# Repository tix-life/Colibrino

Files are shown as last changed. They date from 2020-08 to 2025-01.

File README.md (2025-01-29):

# Colibrino 
Esse é um projeto open-source de uma versão *Faça você mesmo* do nosso mouse de cabeça o Colibri! O objetivo principal dele é promover acessibilidade para pessoas com deficiências físicas do como tetraplegia, artrogripose, amputações e parilisia cerebral.

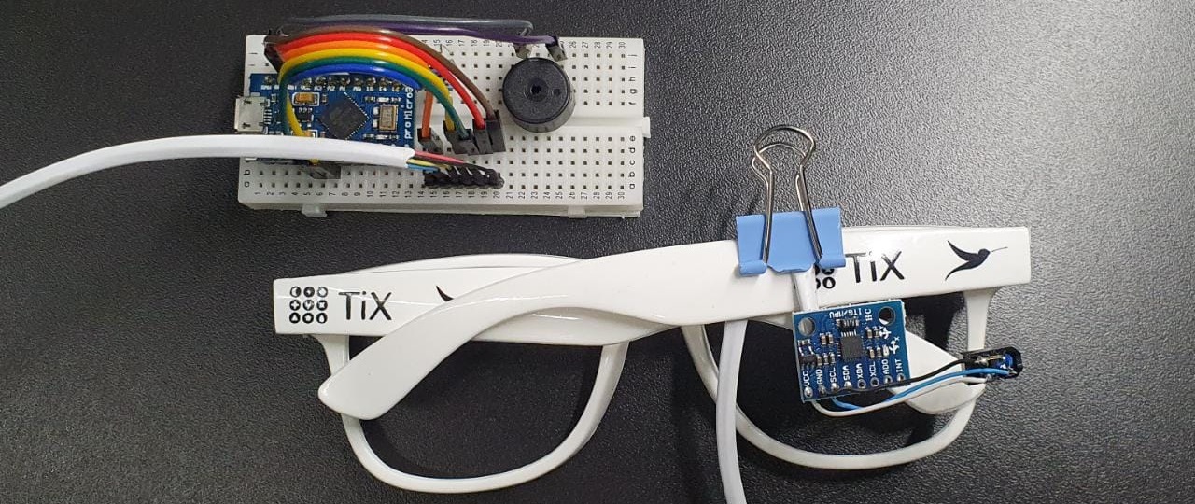
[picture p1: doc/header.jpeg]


[Compartilhe sua montagem e suas dúvidas no nosso fórum!](https://groups.google.com/g/colibrino) 

# Índice 

- [Colibrino](#colibrino)
- [Índice](#índice)
- [Licença de Uso](#licença-de-uso)
- [Materiais](#materiais)
- [Montagem](#montagem)
  - [Diagrama Esquemático](#diagrama-esquemático)
  - [Instruções de Montagem](#instruções-de-montagem)
- [Modo de Uso](#modo-de-uso)
- [Plano de Voo 🐦](#plano-de-voo-)
- [Materiais de referência](#materiais-de-referência)

# Licença de Uso
Este programa é um software livre. Você pode redistribuí-lo e/ou
modificá-lo sob os termos da Licença Pública Geral GNU como publicada
pela Free Software Foundation; na versão 3 da Licença, ou
(a seu critério) qualquer versão posterior.

Este programa é distribuído na esperança de que possa ser útil,
mas SEM NENHUMA GARANTIA; sem uma garantia implícita de ADEQUAÇÃO
a qualquer MERCADO ou APLICAÇÃO EM PARTICULAR. Veja a
[Licença Pública Geral GNU](https://github.com/tix-life/Colibrino/blob/master/LICENSE) para mais detalhes.

# Materiais:

|Nome|Especificação|Documentação|
|---|---|---|
|Arduino Leonardo ou Micro Pro|Com Microcontrolador Atmega 32U4|[Pinagem Pro Micro](https://cdn.sparkfun.com/assets/f/d/8/0/d/ProMicro16MHzv2.pdf)<br>[Pinagem Leonardo](https://content.arduino.cc/assets/Pinout-Leonardo_latest.png)|
|MPU6050|Acelerômetro e Giroscópio|[datasheet](https://invensense.tdk.com/wp-content/uploads/2015/02/MPU-6000-Register-Map1.pdf)|
|TCRT 5000|Sensor Infravermelho|[datasheet](https://www.vishay.com/docs/83760/tcrt5000.pdf)|
|Cabo com 6 vias|Ligação entre o Arduino e os Sensores - |[Ex.: cabo para alarme](https://stecondutores.com.br/produto/cabo-de-alarme/)|
|Placa padrão ou protoboard|Base para montagem do circuito||
|Leds|Indicador de piscada e de funcionamento||
|Resistor|1 x 4700Ω a 6800Ω - polarização do fototransistor <br> 1 x 220Ω a 330Ω - restringe corrente do LED IR<br> 1 x 10Ω - atenuar o  buzzer||
|Buzzer|Indicador Sonoro da Piscada||
|Cabo USB|Conexão entre computador e Arduíno||
|Armação de Óculos|Suporte para os sensores||

# Montagem:

Thumbnail do vídeo (https://www.youtube.com/watch?v=DUF2yonN9Ps)
[Vídeo tutorial](https://www.youtube.com/watch?v=DUF2yonN9Ps)

## Diagrama Esquemático
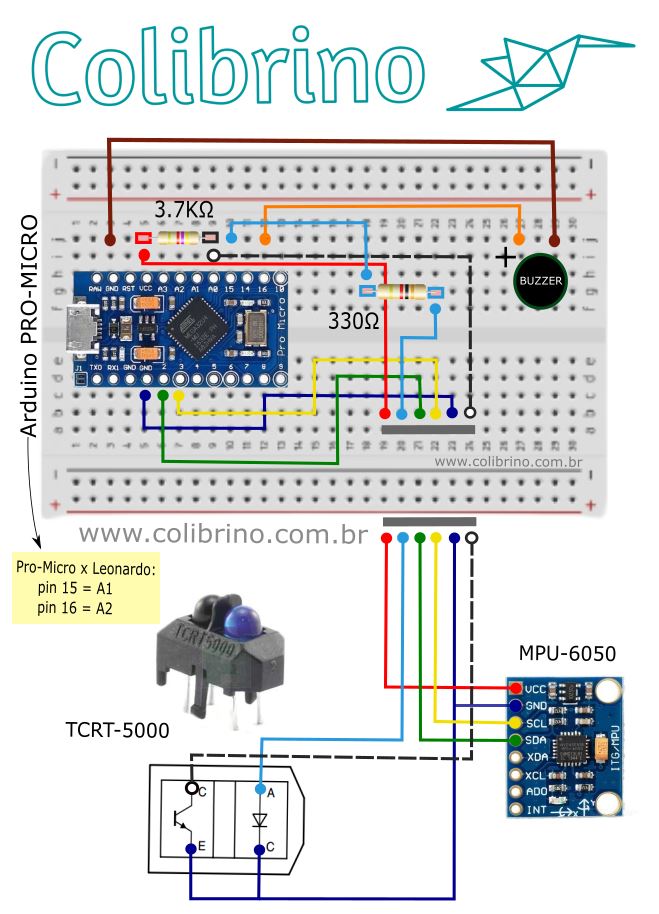
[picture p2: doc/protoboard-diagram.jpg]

## Tabela de Conexões
Nome do Pino no Arduino|Componentes Conectados|Resistor?
|---|---|---|
|VCC (3.3 ou 5V)|MPU-6050 VCC|  |
|VCC (3.3 ou 5V)|TCRT5000 Coletor do Fototransistor| 3500Ω a 5000Ω |
|GND |MPU-6050 GND| |
|GND |TCRT5000 Emissor do Fototransistor| |
|GND |TCRT5000 Cátodo do LED IR (-)|  |
|GND |Buzzer (-)| |
|16 |Buzzer (+)| 0Ω a 10Ω |
|15 |TCRT5000 Ânodo do LED IR (+)| 180Ω a 330Ω |
|A0 |TCRT5000 Coletor do Fototransistor| |

## Instruções de Montagem
1. Conecte o Arduíno, Buzzer, Leds e Resistores no Protoboard. 
2. Para os sensores MPU6050 e TCRT 5000 é necessário solda-los com o fio de 6 vias.
3. Realize as coneções mostradas no diagrama acima.
4. Conecte o Arduíno ao PC usando o cabo USB.
5. Grave o firmware no Arduino usando o [Arduino IDE](https://www.arduino.cc/en/software). No menu "Ferramentas", escolha a opção Arduino Leonardo na lista de placas.
6. Instale o código utilizando o ambiente de desenvolvimento do Arduino devidamente configurado para a placa que está sendo usada.
7. Deixe o Colibrino parado numa mesa sem perturbações até que um beep sonoro indique que ele está pronto para uso (nesse momento ele está calibrando). A calibração é feita apenas uma vez e se não ficar boa (Cursor andando sozinho em alguma direção mesmo o collibrino parado) siga as intruções na seção Calibração.
8. Fixe o sensor MPU6050 em alguma armação de óculos.
9. Use e aproveite. :D
10. [Compartilhe sua montagem e suas dúvidas no nosso fórum!](https://groups.google.com/g/colibrino) 

(montar um painel com imagens)

# Princípios de funcionamento
## Captura do movimento da cabeça
O Colibrino utiliza um tipo de sensor chamado de IMU (Unidade de Medidas Inerciais) para obter informação sobre a orientação espacial da cabeça. A IMU do Colibrino é o MPU-6050, um circuito integrado (acelerômetro + giroscópio) contendo estruturas mecânicas microscópicas capazes de sentir movimentos do corpo preso a ele e a força da gravidade. Essas estruturas mecânicas também interagem eletricamente com o circuito que mede os movimentos em números correspondentes à aceleração e à velocidade angular em três eixos. Os dados são filtrados e utilizados para calcular a posição da cabeça e, por fim, mover o cursor do mouse de forma correspondente.

## Detecção da piscadela
O sensor de piscadelas detecta pequenas variações na reflexão de luz que ocorrem quando uma piscada bem forte é realizada em frente ao sensor. Primeiro a luz infravermelha é emitida por um LED no TCRT5000. A luz é pulsante para que o programa consiga comparar a reflexão com o LED aceso e apagado de forma a compensar variações da luz ambiente. Após ser refletida, a luz é captada por um fototransistor que converte a intensidade da luz em um sinal elétrico medido pelo Arduino.

## ⚠️ Calibração

A calibração efetuada após a primeira gravação do programa no colibrino é feita apenas uma vez. Contudo ela pode falhar devido a movimentações no colibrino durante o processo de calibração, levando a um mau funcionamento do aparelho. Para resolver isso , grave o código LimparCalibração que está dentro da pasta baixada e regrave o código principal mais uma vez. Isso levará o Colibrino para a mesma fase inicial de calibração, repita o procedimento de esperar até que o tempo de calibração conclua.

# Modo de Uso
Com o colibrino devidamente montado para usá-lo basta mexer a cabeça com o oculos que está instalado o sensor. Contudo, segue abaixo uma lista de orientações.

1. O Sensor MPU6050 deve estar colocado no óculos que vai ser usado, porém o TCRT deve estar conectado somente ao fio permitindo o ajuste.
2. Para melhor detecção da piscadela é necessário mexer o fio que o sensor TCRT está conectado para mais próximo ao olho.

(explicar como que usa o colibrino - como posicionar e ajustar o sensor)

# Plano de Voo 🐦
Existe inumeras funções que podem ser adcionadas ao Colibrino e algumas que estão no plano de voo da nossa equipe são:
* Scroll ao inclinar a cabeça para os lados
* Funções com gestos da cabeça

Estamos abertos a sugestões e feedbacks a todos :D 
Agradecemos a leitura <3

# FAQ
* Dúvidas frequentes anexadas no documento abaixo: https://docs.google.com/document/d/1n8rUOnNmSkuknlO98TbDd7EEdKiDvEBH_lRSuz5WyO0/edit?usp=sharing

# Materiais de referência:
* https://www.youtube.com/watch?v=4sIkW7wogrE
* https://github.com/witnessmenow/arduino-switcheroonie/blob/master/BLE-switcheroonie/BLE-switcheroonie.ino
* https://github.com/T-vK/ESP32-BLE-Mouse

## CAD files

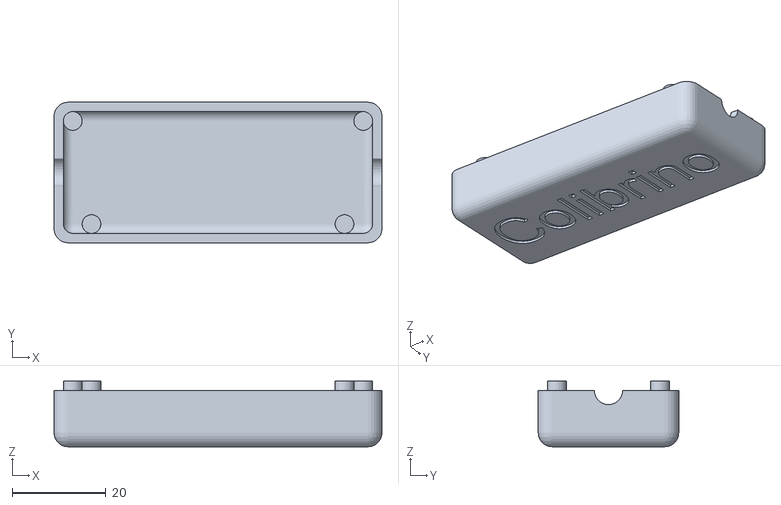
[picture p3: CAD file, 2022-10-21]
3d models/Arduino pro micro box boardless assembly.stl
70.0 x 30.0 x 14.0

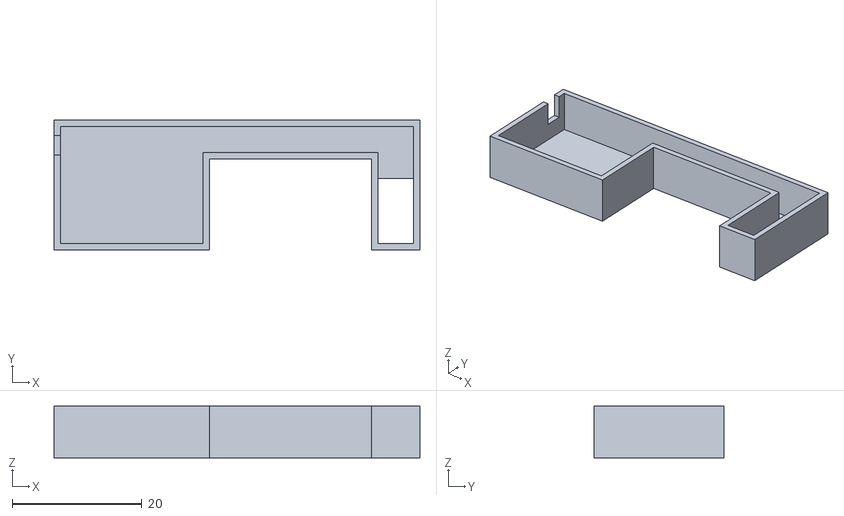
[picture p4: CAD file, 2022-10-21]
3d models/Sensor box IMU and IR part cavity.stl
56.5 x 20.0 x 8.00

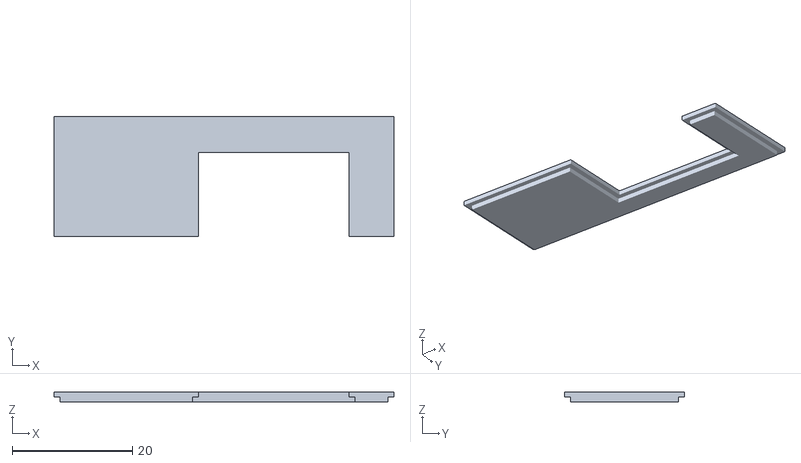
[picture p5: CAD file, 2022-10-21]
3d models/Sensor box IMU and IR part lid.stl
56.5 x 20.0 x 1.60

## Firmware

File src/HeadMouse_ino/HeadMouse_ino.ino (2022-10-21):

// This file is part of the Colibrino project.

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
#include "Mouse.h"
//Carrega a biblioteca Wire
#include <Wire.h>
// #include "filters.h"
#include "MahonyAHRS.h"
#include"mpu6050.h"

//---------------------------------------------------------------------------------------------------
//Definitions
//Mouse
#define SENSIBILIDADE  30
#define TEMPO_DWELL_CICK_MS 1000 
#define DWELL_CICK false
//
#define MPU6050_ACC_GAIN 16384.0
#define MPU6050_GYRO_GAIN 131.072 
/*********************************************************************
 * Global variables
 */
float axR, ayR, azR, gxR, gyR, gzR;
float axg, ayg, azg, gxrs, gyrs, gzrs;
//float ax_filtro, ay_filtro, az_filtro, gx_filtro, gy_filtro, gz_filtro;
bool conectado = false;
//float yaw_filtro, pitch_filtro, roll_filtro;
const int MPU_addr=0x68;  // I2C address of the MPU-6050
/*********************************************************************
 * External variables
 */
extern int16_t AcX, AcY, AcZ, Tmp, GyX, GyY, GyZ;
extern float yaw_mahony,pitch_mahony,roll_mahony;
//Objects
// BleMouse bleMouse;
// filters pbax,pbay,pbaz,pbgx,pbgy,pbgz;

#define INTERRUPT_PIN 7 // use pin 2 on Arduino Uno & most boards
#define LED_PIN 8 // (Arduino is 13, Teensy is 11, Teensy++ is 6)

#define ON true
#define OFF false
int g_clique = 0;
void filtraIMU()
{
  //Filtro 2 ordem
  // ax_filtro= filtro_2PB10Hz(AcX, pbax);
  // ay_filtro= filtro_2PB10Hz(AcY, pbay);
  // az_filtro= filtro_2PB10Hz(AcZ, pbaz);
  // gx_filtro= filtro_2PB10Hz(GyX, pbgx);
  // gy_filtro= filtro_2PB10Hz(GyY, pbgy);
  // gz_filtro= filtro_2PB10Hz(GyZ, pbgz);
  
  //Converte
  axg = (float)(AcX /*- LSM6DSM_AXOFFSET*/) / MPU6050_ACC_GAIN;
  ayg = (float)(AcY /*- LSM6DSM_AYOFFSET*/) / MPU6050_ACC_GAIN;
  azg = (float)(AcZ /*- LSM6DSM_AZOFFSET*/) / MPU6050_ACC_GAIN;
  gxrs = (float)(GyX - (0)) / MPU6050_GYRO_GAIN * 0.01745329; //degree to radians
  gyrs = (float)(GyY - (0)) / MPU6050_GYRO_GAIN * 0.01745329; //degree to radians
  gzrs = (float)(GyZ - (0)) / MPU6050_GYRO_GAIN * 0.01745329; //degree to radians
  // Degree to Radians Pi / 180 = 0.01745329 0.01745329251994329576923690768489
}
float corrigeYaw(float sinal)
{
  static float valorDeriv = 0, zero = 0;
  static float sinalCorrigido=0, offset = 0;
  static float  sinalAnterior = 0;
  static int s=1,d=-1;
  
  valorDeriv = (sinal - zero);
  zero = sinal;
  
  if(valorDeriv <= -180)
  {
      offset += +360.0f;
  }
  else if(valorDeriv >= 180)
  {
      offset += -360.0f;
  }
  sinalCorrigido = sinal;
  sinalCorrigido += offset;
  
  return sinalCorrigido;
}
int8_t mouseHoriz(void)
{
  static float horzZero =0.0f;
  static float horzValue = 0.0f;  // Stores current analog output of each axis
  static float yaw_corrigido = 0.0f;
  static int amostragem = 5;
  yaw_corrigido = corrigePitch(yaw_mahony);
  
  if(--amostragem == 0)
  {
    amostragem = 5;
    horzValue = (yaw_corrigido - horzZero)*SENSIBILIDADE;
    horzZero = yaw_corrigido;
  }
  return horzValue;
}
float corrigePitch(float sinal)
{
  static float valorDeriv = 0, zero = 0;
  static float sinalCorrigido=0, offset = 0;
  static float  sinalAnterior = 0;
  static int s=1,d=-1;
  
  valorDeriv = (sinal - zero);
  zero = sinal;

  if(valorDeriv <= -180)
  {
      offset += +360.0f;
  }
  else if(valorDeriv >= 180)
  {
      offset += -360.0f;
  }
  sinalCorrigido = sinal;
  sinalCorrigido += offset;
  
  return sinalCorrigido;
}
int8_t mouseVert(void)
{
  static float vertZero =0.0f;
  static float vertValue = 0.0f;  // Stores current analog output of each axis
  static float pitch_corrigido = 0.0f;
  static int amostragem = 5;
  pitch_corrigido = corrigePitch(pitch_mahony);
  if(--amostragem == 0)
  {
    amostragem = 5;
    vertValue = (pitch_corrigido - vertZero)*SENSIBILIDADE;
    vertZero = pitch_corrigido;
  }
  return vertValue;
}


/*********************************************************************
 * @fn      scrollDetector
 * 
 * @brief   Ativa ou reativa o Colibri de acordo com a 
 *          sequencia de movimentos feita
 *
 * @param   horz - derivada do Yaw
 * @param   verti - derivada do Pitch
 *
 * @return  ligado - flag para ativar/desativar o colibri.
 */
#define RMEDIA 0.001f
#define RMARGEM 4
int scrollDetector() {
  static float rmedia = 90;
  static uint32_t timer1 = 0;
  int diferenca;
  
  diferenca = roll_mahony - rmedia;
  
  
            //SendInt(diferenca);
         //SendLineEnd();
  
  if (abs(diferenca) < RMARGEM) {
    rmedia = ((1 - RMEDIA) * rmedia) + (RMEDIA * roll_mahony);
    timer1 = millis();
    return 0;
  }
  else if (abs(diferenca) > 2.5*RMARGEM) { // Ignora roll muito grande
    if (millis() - timer1 > 5000) {       // Reseta média se ficar muito tempo com roll alto
      rmedia = roll_mahony;
      timer1 = millis();
    }
    return 0;
  }
  else if (millis() - timer1 > 200) {
    timer1 = millis();
    if (diferenca > 0) {
      return 1 ;//+ (2 * diferenca / RMARGEM);
    }
    else {
      return -1;// + (2 * diferenca / RMARGEM);
    }
  }
  return 0;
}
int tabelaGestos[6][2]={0,0,0,0,0,0};
int tabelaMOV[6][2]={0,0,0,0,0,0};
int8_t VG[4]={0,0,0};
#define NADA        0
#define ESQUERDA    1
#define DIREITA     2
#define CIMA        3
#define BAIXO       4
#define SCROLL_ESQ  5
#define SCROLL_DIR  6
#define DESLIGA     ESQUERDA
#define LIGA        CIMA
#define SCROLL      SCROLL_ESQ  
#define TIMEOUT_MOVE 110 //Tempo entre movimentos
bool g_atividade = 0;
bool atividade = true;

#define INVALIDO    0
#define SIM         1
#define NAO         2
enum
{
  Estado_movimentov2 = 0,
  Estado_passaNaZm,
};
int8_t coletaMovimentos(float horz, float vert)
{
  int8_t movimento = 0;
  static int estado = 0, tipo = 0,tipo_1=0,tipo_2=0;
  switch (estado)
  {
    case Estado_movimentov2:
      movimento = 0;
      tipo =0;
      tipo_1=0;tipo_2=0;
      if(horz> 1.0f)
      {
        tipo =  DIREITA;
        estado = Estado_passaNaZm;
      }
      else if(horz< -1.0f)
      {
        tipo =  ESQUERDA;
        estado = Estado_passaNaZm;
      }
      else if(vert > 0.75f)
      {
        tipo =  CIMA;
        estado = Estado_passaNaZm;
      }
      else if(vert< -0.75f)
      {
        tipo =  BAIXO;  
        estado = Estado_passaNaZm;
      }

      // if(tipo_1!= 0 || tipo_2 !=0)
      // {
      //   if(abs_float(horz) >= abs_float(vert) )
      //   {
      //     tipo = tipo_1 ;
      //   }
      //   if(abs_float(vert) >= abs_float(horz) )
      //   {
      //     tipo = tipo_2 ;
      //   }

      //   estado = Estado_passaNaZm;
      // }
      break;
    case Estado_passaNaZm:
      
      if(tipo == DIREITA)
      {
        if(horz< 1.0f)
        {
          estado = Estado_movimentov2;
          movimento = tipo;
        }
      }
      else if(tipo == ESQUERDA)
      {
        if(horz> (-1.0f))
        {
          estado = Estado_movimentov2;
          movimento = tipo;
        }
      }
      else if(tipo == CIMA)
      {
        if(vert < 0.75f)
        {
          estado = Estado_movimentov2;
          movimento = tipo;
        }
      }
      else if(tipo == BAIXO)
      {
        if(vert > (-0.75f))
        {
          estado = Estado_movimentov2;
          movimento = tipo;
        }
      }
      
      break;
    
    default:
      break;
  }
  return movimento;
}

int8_t regrideIndice(int8_t indice, int8_t casas)
{
  int8_t resultado = 0;
  resultado =  indice;
  for (int i = 0; i < casas; i++)
  {
    if(resultado == 0)
    {
        resultado = 5;
    }
    else
    {
        resultado--;
    }
  }
  
  return resultado;
}
int8_t progrideIndice(int8_t indice)
{
  int8_t resultado = 0;
  resultado =  indice;

  if(resultado == 5)
  {
    resultado = 0;
  }
  else
  {
    resultado++;
  }
  
  return resultado;
}

int calculaTempo(int valorIntervalo)
{
  int tempoCerto =0;
  tempoCerto = (int)(valorIntervalo);
  return tempoCerto;
}
int8_t analisaVetor()
{
  int8_t resultado = INVALIDO;
  if(VG[0]==ESQUERDA && VG[1]==DIREITA && VG[2]==ESQUERDA && VG[3]==DIREITA )
  {
    resultado = NAO;
  }
  else if(VG[0]==DIREITA && VG[1]==ESQUERDA && VG[2]==DIREITA && VG[3]==ESQUERDA )
  {
    resultado = NAO;
  }
  else if(VG[0]==CIMA && VG[1]==BAIXO && VG[2]==CIMA )
  {
    resultado = SIM;
  }
  else if(VG[0]==BAIXO && VG[1]==CIMA && VG[2]==BAIXO )
  {
    resultado = SIM;
  }
  else
  { 
    resultado = INVALIDO;
  }
  return resultado;
}
enum
{
  Estado_novoGesto = 0,
  Estado_reduzIndice,
  Estado_calculaIntervalo_1,
  Estado_calculaIntervalo_2,
  Estado_calculaIntervalo_3,
  Estado_calculaIntervalo_Total,
  Estado_analisaVetor,
};
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

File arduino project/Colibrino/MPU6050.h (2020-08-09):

#include <Wire.h>
// Definitions

// Definitions referenced Jeff Rowberg's MPU6050.h
#define MPU6050_ADDRESS_AD0_LOW     0x68 // address pin low (GND), default for InvenSense evaluation board
#define MPU6050_ADDRESS_AD0_HIGH    0x69 // address pin high (VCC)
#define MPU6050_DEFAULT_ADDRESS     MPU6050_ADDRESS_AD0_LOW

#define MPU6050_ACC_GAIN 16384.0 // AFS_SEL = 0, +/-2g, MPU6050_ACCEL_FS_2
#define MPU6050_ACC_GAIN 16384.0 // AFS_SEL = 0, +/-2g, MPU6050_ACCEL_FS_2
#define MPU6050_ACC_GAIN 16384.0 // AFS_SEL = 0, +/-2g, MPU6050_ACCEL_FS_2
//#define MPU6050_ACC_GAIN 8192.0 // AFS_SEL = 1, +/-4g, MPU6050_ACCEL_FS_4
//#define MPU6050_ACC_GAIN 8192.0 // AFS_SEL = 1, +/-4g, MPU6050_ACCEL_FS_4
//#define MPU6050_ACC_GAIN 8192.0 // AFS_SEL = 1, +/-4g, MPU6050_ACCEL_FS_4
// #define MPU6050_ACC_GAIN 4096.0 // AFS_SEL = 2, +/-8g, MPU6050_ACCEL_FS_8     /Coreano
// #define MPU6050_ACC_GAIN 4096.0 // AFS_SEL = 2, +/-8g, MPU6050_ACCEL_FS_8
// #define MPU6050_ACC_GAIN 4096.0 // AFS_SEL = 2, +/-8g, MPU6050_ACCEL_FS_8
//#define MPU6050_ACC_GAIN 2048.0 // AFS_SEL = 3, +/-16g, MPU6050_ACCEL_FS_16
//#define MPU6050_ACC_GAIN 2048.0 // AFS_SEL = 3, +/-16g, MPU6050_ACCEL_FS_16
//#define MPU6050_ACC_GAIN 2048.0 // AFS_SEL = 3, +/-16g, MPU6050_ACCEL_FS_16
//#define MPU6050_GXOFFSET 0
//#define MPU6050_GYOFFSET 0
//#define MPU6050_GZOFFSET 0
#define MPU6050_GYRO_GAIN 131.072 // FS_SEL = 0, +/-250degree/s, MPU6050_GYRO_FS_250
#define MPU6050_GYRO_GAIN 131.072 // FS_SEL = 0, +/-250degree/s, MPU6050_GYRO_FS_250
#define MPU6050_GYRO_GAIN 131.072 // FS_SEL = 0, +/-250degree/s, MPU6050_GYRO_FS_250
//#define MPU6050_GYRO_GAIN 65.536 // FS_SEL = 1, +/-500degree/s, MPU6050_GYRO_FS_500
//#define MPU6050_GYRO_GAIN 65.536 // FS_SEL = 1, +/-500degree/s, MPU6050_GYRO_FS_500
//#define MPU6050_GYRO_GAIN 65.536 // FS_SEL = 1, +/-500degree/s, MPU6050_GYRO_FS_500
//#define MPU6050_GYRO_GAIN 32.768 // FS_SEL = 2, +/-1000degree/s, MPU6050_GYRO_FS_1000
//#define MPU6050_GYRO_GAIN 32.768 // FS_SEL = 2, +/-1000degree/s, MPU6050_GYRO_FS_1000
//#define MPU6050_GYRO_GAIN 32.768 // FS_SEL = 2, +/-1000degree/s, MPU6050_GYRO_FS_1000
// #define MPU6050_GYRO_GAIN 16.384 // FS_SEL = 3, +/-2000degree/s, MPU6050_GYRO_FS_2000 Coreano
// #define MPU6050_GYRO_GAIN 16.384 // FS_SEL = 3, +/-2000degree/s, MPU6050_GYRO_FS_2000
// #define MPU6050_GYRO_GAIN 16.384 // FS_SEL = 3, +/-2000degree/s, MPU6050_GYRO_FS_2000

#define MPU6050_RA_XG_OFFS_TC       0x00 //[7] PWR_MODE, [6:1] XG_OFFS_TC, [0] OTP_BNK_VLD
#define MPU6050_RA_YG_OFFS_TC       0x01 //[7] PWR_MODE, [6:1] YG_OFFS_TC, [0] OTP_BNK_VLD
#define MPU6050_RA_ZG_OFFS_TC       0x02 //[7] PWR_MODE, [6:1] ZG_OFFS_TC, [0] OTP_BNK_VLD
#define MPU6050_RA_X_FINE_GAIN      0x03 //[7:0] X_FINE_GAIN
#define MPU6050_RA_Y_FINE_GAIN      0x04 //[7:0] Y_FINE_GAIN
#define MPU6050_RA_Z_FINE_GAIN      0x05 //[7:0] Z_FINE_GAIN
#define MPU6050_RA_XA_OFFS_H        0x06 //[15:0] XA_OFFS
#define MPU6050_RA_XA_OFFS_L_TC     0x07
#define MPU6050_RA_YA_OFFS_H        0x08 //[15:0] YA_OFFS
#define MPU6050_RA_YA_OFFS_L_TC     0x09
#define MPU6050_RA_ZA_OFFS_H        0x0A //[15:0] ZA_OFFS
#define MPU6050_RA_ZA_OFFS_L_TC     0x0B
#define MPU6050_RA_SELF_TEST_X      0x0D //[7:5] XA_TEST[4-2], [4:0] XG_TEST[4-0]
#define MPU6050_RA_SELF_TEST_Y      0x0E //[7:5] YA_TEST[4-2], [4:0] YG_TEST[4-0]
#define MPU6050_RA_SELF_TEST_Z      0x0F //[7:5] ZA_TEST[4-2], [4:0] ZG_TEST[4-0]
#define MPU6050_RA_SELF_TEST_A      0x10 //[5:4] XA_TEST[1-0], [3:2] YA_TEST[1-0], [1:0] ZA_TEST[1-0]
#define MPU6050_RA_XG_OFFS_USRH     0x13 //[15:0] XG_OFFS_USR
#define MPU6050_RA_XG_OFFS_USRL     0x14
#define MPU6050_RA_YG_OFFS_USRH     0x15 //[15:0] YG_OFFS_USR
#define MPU6050_RA_YG_OFFS_USRL     0x16
#define MPU6050_RA_ZG_OFFS_USRH     0x17 //[15:0] ZG_OFFS_USR
#define MPU6050_RA_ZG_OFFS_USRL     0x18
#define MPU6050_RA_SMPLRT_DIV       0x19
#define MPU6050_RA_CONFIG           0x1A
#define MPU6050_RA_GYRO_CONFIG      0x1B
#define MPU6050_RA_ACCEL_CONFIG     0x1C
#define MPU6050_RA_FF_THR           0x1D
#define MPU6050_RA_FF_DUR           0x1E
#define MPU6050_RA_MOT_THR          0x1F
#define MPU6050_RA_MOT_DUR          0x20
#define MPU6050_RA_ZRMOT_THR        0x21
#define MPU6050_RA_ZRMOT_DUR        0x22
#define MPU6050_RA_FIFO_EN          0x23
#define MPU6050_RA_I2C_MST_CTRL     0x24
#define MPU6050_RA_I2C_SLV0_ADDR    0x25
#define MPU6050_RA_I2C_SLV0_REG     0x26
#define MPU6050_RA_I2C_SLV0_CTRL    0x27
#define MPU6050_RA_I2C_SLV1_ADDR    0x28
#define MPU6050_RA_I2C_SLV1_REG     0x29
#define MPU6050_RA_I2C_SLV1_CTRL    0x2A
#define MPU6050_RA_I2C_SLV2_ADDR    0x2B
#define MPU6050_RA_I2C_SLV2_REG     0x2C
#define MPU6050_RA_I2C_SLV2_CTRL    0x2D
#define MPU6050_RA_I2C_SLV3_ADDR    0x2E
#define MPU6050_RA_I2C_SLV3_REG     0x2F
#define MPU6050_RA_I2C_SLV3_CTRL    0x30
#define MPU6050_RA_I2C_SLV4_ADDR    0x31
#define MPU6050_RA_I2C_SLV4_REG     0x32
#define MPU6050_RA_I2C_SLV4_DO      0x33
#define MPU6050_RA_I2C_SLV4_CTRL    0x34
#define MPU6050_RA_I2C_SLV4_DI      0x35
#define MPU6050_RA_I2C_MST_STATUS   0x36
#define MPU6050_RA_INT_PIN_CFG      0x37
#define MPU6050_RA_INT_ENABLE       0x38
#define MPU6050_RA_DMP_INT_STATUS   0x39
#define MPU6050_RA_INT_STATUS       0x3A
#define MPU6050_RA_ACCEL_XOUT_H     0x3B
#define MPU6050_RA_ACCEL_XOUT_L     0x3C
#define MPU6050_RA_ACCEL_YOUT_H     0x3D
#define MPU6050_RA_ACCEL_YOUT_L     0x3E
#define MPU6050_RA_ACCEL_ZOUT_H     0x3F
#define MPU6050_RA_ACCEL_ZOUT_L     0x40
#define MPU6050_RA_TEMP_OUT_H       0x41
#define MPU6050_RA_TEMP_OUT_L       0x42
#define MPU6050_RA_GYRO_XOUT_H      0x43
#define MPU6050_RA_GYRO_XOUT_L      0x44
#define MPU6050_RA_GYRO_YOUT_H      0x45
#define MPU6050_RA_GYRO_YOUT_L      0x46
#define MPU6050_RA_GYRO_ZOUT_H      0x47
#define MPU6050_RA_GYRO_ZOUT_L      0x48
#define MPU6050_RA_EXT_SENS_DATA_00 0x49
#define MPU6050_RA_EXT_SENS_DATA_01 0x4A
#define MPU6050_RA_EXT_SENS_DATA_02 0x4B
#define MPU6050_RA_EXT_SENS_DATA_03 0x4C
#define MPU6050_RA_EXT_SENS_DATA_04 0x4D
#define MPU6050_RA_EXT_SENS_DATA_05 0x4E
#define MPU6050_RA_EXT_SENS_DATA_06 0x4F
#define MPU6050_RA_EXT_SENS_DATA_07 0x50
#define MPU6050_RA_EXT_SENS_DATA_08 0x51
#define MPU6050_RA_EXT_SENS_DATA_09 0x52
#define MPU6050_RA_EXT_SENS_DATA_10 0x53
#define MPU6050_RA_EXT_SENS_DATA_11 0x54
#define MPU6050_RA_EXT_SENS_DATA_12 0x55
#define MPU6050_RA_EXT_SENS_DATA_13 0x56
#define MPU6050_RA_EXT_SENS_DATA_14 0x57
#define MPU6050_RA_EXT_SENS_DATA_15 0x58
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

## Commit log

2020-07-15 Pastas dos arquivos e código para arduino
2020-08-08 Inclusão de classe para filtros de 2 ordem, filtro de mahony e calculo de angulos de euler. Em testes
2020-08-09 Uso de filtros do próprio MPU6050
2020-08-09 Remoção hardcode de offsets do giroscópio
2020-08-09 Uso de yaw e pitch para controlar mouse BLE
2020-08-10 Reset depois de desconectar
2020-08-10 Início da implementação de clique por acionador externo
2020-08-24 Máquina de estados para clique
2021-07-01 Adição de arquivos da biblioteca do MPU e i2c
2021-07-02 Uso de filtro mahony
2021-07-02 Adiciona detecção de piscadelas via TCRT5000. Ainda não está conectado com o clique do mouse
2021-07-04 Versão baseada com detecção de piscadela funcionando, porém com muito falso positivo e demandando calibração. Baseada em código de testes muito antigo
2021-07-05 Conversão da condificação dos arquivos para UTF-8 Troquei o código experimental da detecção de piscadelas por uma mversão mais robusta e que não necessita de procedimento de calibração. Modifiquei o 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
2021-07-06 Reduz um pouco a sensibilidade para início da piscadela; Rotaciona referencial do acelerômetro para que a PCB do MPU6050 fique paralela à vertical. Antes o plano contendo a PCB tinha que ficar na hor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
2021-07-09 Mais melhorias na documentação: tabela de componentes e descrição do funcionamento
2021-07-27 Adicionei uma tabela de conexões na documentação
2021-08-11 BUGFIX: O sensor estava disparando constantemente quando não havia nenhum anteparo na frente. Isso ocorria em conjunto com valores negativos de "sensorValue" quando o sinal ficava próximo de zero. Ag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
2021-08-14 Resolve inconsistencias nos valores de resistores listados na documenttação; Adiciona anúncio do tipo de licença no topo do arquivo principal do projeto HeadMouse_ino.ino
2021-08-30 Ajuestei os parâmetros de sensibilidade da detecção para que o encerramento do clique seja mais fácil. Estava muito frequente o cluique ficar segurado quando não deveria e muito difícil dar um clique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
2021-08-30 Instruções sobre a seleção de placas na IDE do arduino
2022-01-20 New wiring diagram
2022-10-21 Adição do modo de clique automático / dwell crique. Nesse modo o clique ocorre sempre que o cursor cessa um movimento e permacece estacionado por determinado tempo (1000ms) com esse modo ativo o sens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
2022-10-21 correção de erro em que o clique automático não é disparado após um movimento apenas no eixo vertical; Clique automático desligado por padrão. Use a definição DWELL_CICK para ativar
2022-10-21 Organização do repositório, auto-formatação do arquivo principal do Arduino e atualização do projeto conforme recomendações da nova IDE Arduino 2.0
    [Arduino pro micro box boardless assembly.stl, Sensor box IMU and IR part cavity.stl, Sensor box IMU and IR part lid.stl]
2023-01-25 Arquivo para limpeza de calibração

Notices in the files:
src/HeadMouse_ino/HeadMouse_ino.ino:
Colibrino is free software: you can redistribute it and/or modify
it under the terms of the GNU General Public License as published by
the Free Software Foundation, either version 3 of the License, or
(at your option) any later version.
